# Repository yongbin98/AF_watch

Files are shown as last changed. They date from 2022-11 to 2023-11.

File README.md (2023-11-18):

# BAMI_watch

This repository contains the C code used in the PPG/ECG Wearable Devices for Atrial Fibrillation Diagnosis System thesis study. 

The code is designed for a smartwatch equipped with the following components:
- PPG sensor: MAX86171
- ECG sensor: MAX30003
- IMU sensor: LSM6DS
- LCD display: ST7789
- Battery monitoring chip: MAX17262
- Bluetooth module: E104-BT5005A
- Other components: SD card, switch, speaker

The following protocols are used:
- SD card: Fatfs
- ARM::CMSIS: ver 5.8.0
- ARM::DSP: ver 1.9.0

The hardware architectures:


The Developed wearable watch :


The code was developed in the Keil IDE.

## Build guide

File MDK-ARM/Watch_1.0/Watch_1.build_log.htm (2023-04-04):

µVision Build Log

Tool Versions:

IDE-Version: ¥ìVision V5.36.0.0
Copyright (C) 2021 ARM Ltd and ARM Germany GmbH. All rights reserved.
License Information: l l, l, LIC=3UURY-IHUXV-YDFK5-G8043-GK9D9-KWBGT
 
Tool Versions:
Toolchain:       MDK-ARM Professional  Version: 5.36.0.0
Toolchain Path:  C:\Keil_v5\ARM\ARMCC\Bin
C Compiler:      Armcc.exe V5.06 update 7 (build 960)
Assembler:       Armasm.exe V5.06 update 7 (build 960)
Linker/Locator:  ArmLink.exe V5.06 update 7 (build 960)
Library Manager: ArmAr.exe V5.06 update 7 (build 960)
Hex Converter:   FromElf.exe V5.06 update 7 (build 960)
CPU DLL:         SARMCM3.DLL V5.36.0.0
Dialog DLL:      DCM.DLL V1.17.3.0
Target DLL:      STLink\ST-LINKIII-KEIL_SWO.dll V3.0.9.0
Dialog DLL:      TCM.DLL V1.53.0.0

Project:

C:\Users\AW_Lab_LYB\Documents\STM32\Watch_V2.3 (Prototype)\MDK-ARM\Watch_1.0.uvprojx
Project File Date:  01/26/2023

Output:

*** Using Compiler 'V5.06 update 7 (build 960)', folder: 'C:\Keil_v5\ARM\ARMCC\Bin'
Build target 'Watch_1.0'
compiling MAX30003.c...
../Drivers/CMSIS/Device/ST/STM32F4xx/Include/stm32f413xx.h(52): warning:  #47-D: incompatible redefinition of macro "__FPU_PRESENT" 
  #define __FPU_PRESENT             1U       /*!< FPU present                                   */
..\Lib\MAX30003.c: 1 warning, 0 errors
compiling lcdscreen.c...
../Drivers/CMSIS/Device/ST/STM32F4xx/Include/stm32f413xx.h(52): warning:  #47-D: incompatible redefinition of macro "__FPU_PRESENT" 
  #define __FPU_PRESENT             1U       /*!< FPU present                                   */
..\Lib\lcdscreen.h(28): warning:  #1-D: last line of file ends without a newline
  #endif
..\Lib\lcdscreen.c(432): warning:  #1-D: last line of file ends without a newline
  }
..\Lib\lcdscreen.c: 3 warnings, 0 errors
linking...
Program Size: Code=86910 RO-data=247570 RW-data=252 ZI-data=181308  
FromELF: creating hex file...
"Watch_1.0\Watch_1.0" - 0 Error(s), 4 Warning(s).

Software Packages used:

Package Vendor: ARM
                http://www.keil.com/pack/ARM.CMSIS.5.8.0.pack
                ARM.CMSIS.5.8.0
                CMSIS (Common Microcontroller Software Interface Standard)
   * Component: CORE Version: 5.5.0

Package Vendor: Keil
                https://www.keil.com/pack/Keil.ARM_Compiler.1.7.1.pack
                Keil.ARM_Compiler.1.7.1
                Keil ARM Compiler extensions for ARM Compiler 5 and ARM Compiler 6
   * Component: STDERR Variant: ITM Version: 1.2.0
   * Component: STDIN Variant: ITM Version: 1.2.0
   * Component: STDOUT Variant: ITM Version: 1.2.0

Package Vendor: Keil
                http://www.keil.com/pack/Keil.STM32F4xx_DFP.2.16.0.pack
                Keil.STM32F4xx_DFP.2.16.0
                STMicroelectronics STM32F4 Series Device Support, Drivers and Examples

Collection of Component include folders:

  .\RTE\_Watch_1.0
  C:\Users\AW_Lab_LYB\AppData\Local\Arm\Packs\ARM\CMSIS\5.8.0\CMSIS\Core\Include
  C:\Users\AW_Lab_LYB\AppData\Local\Arm\Packs\Keil\STM32F4xx_DFP\2.16.0\Drivers\CMSIS\Device\ST\STM32F4xx\Include

Collection of Component Files used:

   * Component: ARM::CMSIS:CORE:5.5.0
      Include file:  CMSIS\Core\Include\tz_context.h

   * Component: Keil.ARM Compiler::Compiler:I/O:STDERR:ITM:1.2.0
      Source file:   Source\retarget_io.c

   * Component: Keil.ARM Compiler::Compiler:I/O:STDIN:ITM:1.2.0
      Source file:   Source\retarget_io.c

   * Component: Keil.ARM Compiler::Compiler:I/O:STDOUT:ITM:1.2.0
      Source file:   Source\retarget_io.c
Build Time Elapsed:  00:00:02

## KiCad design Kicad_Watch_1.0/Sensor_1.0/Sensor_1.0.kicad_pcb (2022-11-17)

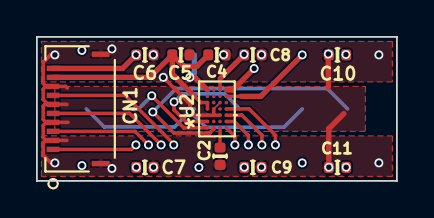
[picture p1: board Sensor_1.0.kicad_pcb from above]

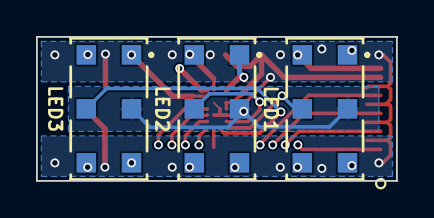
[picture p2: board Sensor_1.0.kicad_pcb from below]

Board: 4 copper layers, 20.0 x 8.0 mm, 14 parts (3 on the bottom side), 14 nets.

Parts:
C2: 1u; UL_C_0402_1005Metric
C4: 10u; UL_C_0402_1005Metric
C5: 0.1u; UL_C_0402_1005Metric
C6, C7, C8, C9, C10, C11: 22u; UL_C_0402_1005Metric
CN1: 503480-1000
LED1, LED2, LED3: SFH_7070; SFH7070
U2: MAX86171ENI+; MAX86171ENI&plus_

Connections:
+1V8: C4.1, C5.1, CN1.9, U2.D3 (VDD_ANA), U2.D4 (VDD_DIG)
/LED3_DRV: LED1.1, LED1.3, U2.A1 (LED3_DRV)
/LED4_DRV: LED2.1, LED2.3, U2.D1 (LED4_DRV)
/LED9_DRV: LED3.1, LED3.3, U2.A2 (LED9_DRV)
/PD1_IN: LED1.5, U2.D7 (PD1_IN)
/PD2_IN: LED2.5, U2.D6 (PD2_IN)
/PD3_IN: LED3.5, U2.C7 (PD3_IN)
/PPG_CS: CN1.7, U2.A7 (CSB/ADDR)
/PPG_MISO: CN1.3, U2.A5 (SDO)
/PPG_MOSI: CN1.5, U2.A6 (SDI/SDA)
/PPG_SCLK: CN1.1, U2.A4 (SCLK/SCL)
unnamed: C2.1, U2.B7 (VREF)
U_GND: C2.2, C4.2, C5.2, C6.2, C7.2, C8.2, C9.2, C10.2, C11.2, CN1.2, CN1.4, CN1.6, CN1.8, CN1.11, CN1.12, LED1.2, LED2.2, LED3.2, U2.B3 (PGND), U2.B5 (TRIG), U2.C4 (I2C_SEL), U2.C5 (GND), U2.D5 (PD_GND)
VDD: C6.1, C7.1, C8.1, C9.1, C10.1, C11.1, CN1.10, LED1.4, LED1.6, LED2.4, LED2.6, LED3.4, LED3.6, U2.B1 (VLED)

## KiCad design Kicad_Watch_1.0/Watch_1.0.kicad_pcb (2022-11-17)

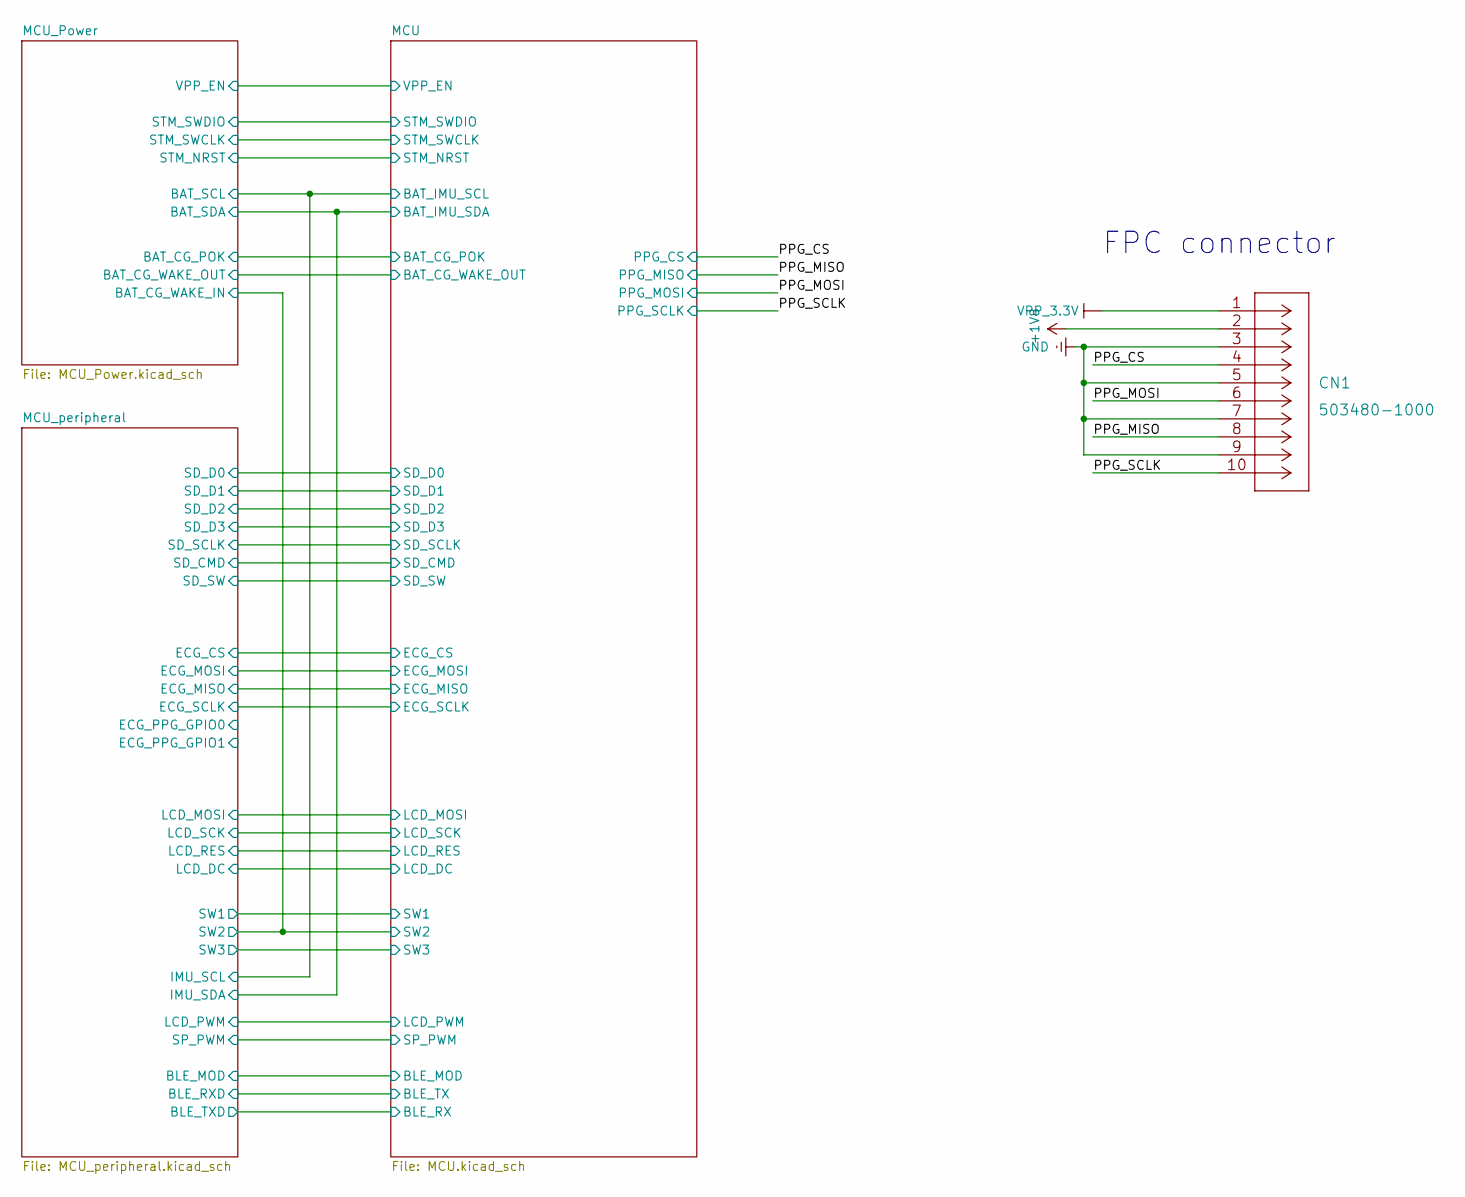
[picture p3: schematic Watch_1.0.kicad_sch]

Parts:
CN1: 503480-1000

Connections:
+1V8: CN1.2; also elsewhere on the board
/PPG_CS: CN1.4; also elsewhere on the board
/PPG_MISO: CN1.8; also elsewhere on the board
/PPG_MOSI: CN1.6; also elsewhere on the board
/PPG_SCLK: CN1.10; also elsewhere on the board
U_GND: CN1.3, CN1.5, CN1.7, CN1.9, CN1.11, CN1.12; also elsewhere on the board
VPP_3_3V: CN1.1; also elsewhere on the board

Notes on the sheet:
FPC connector

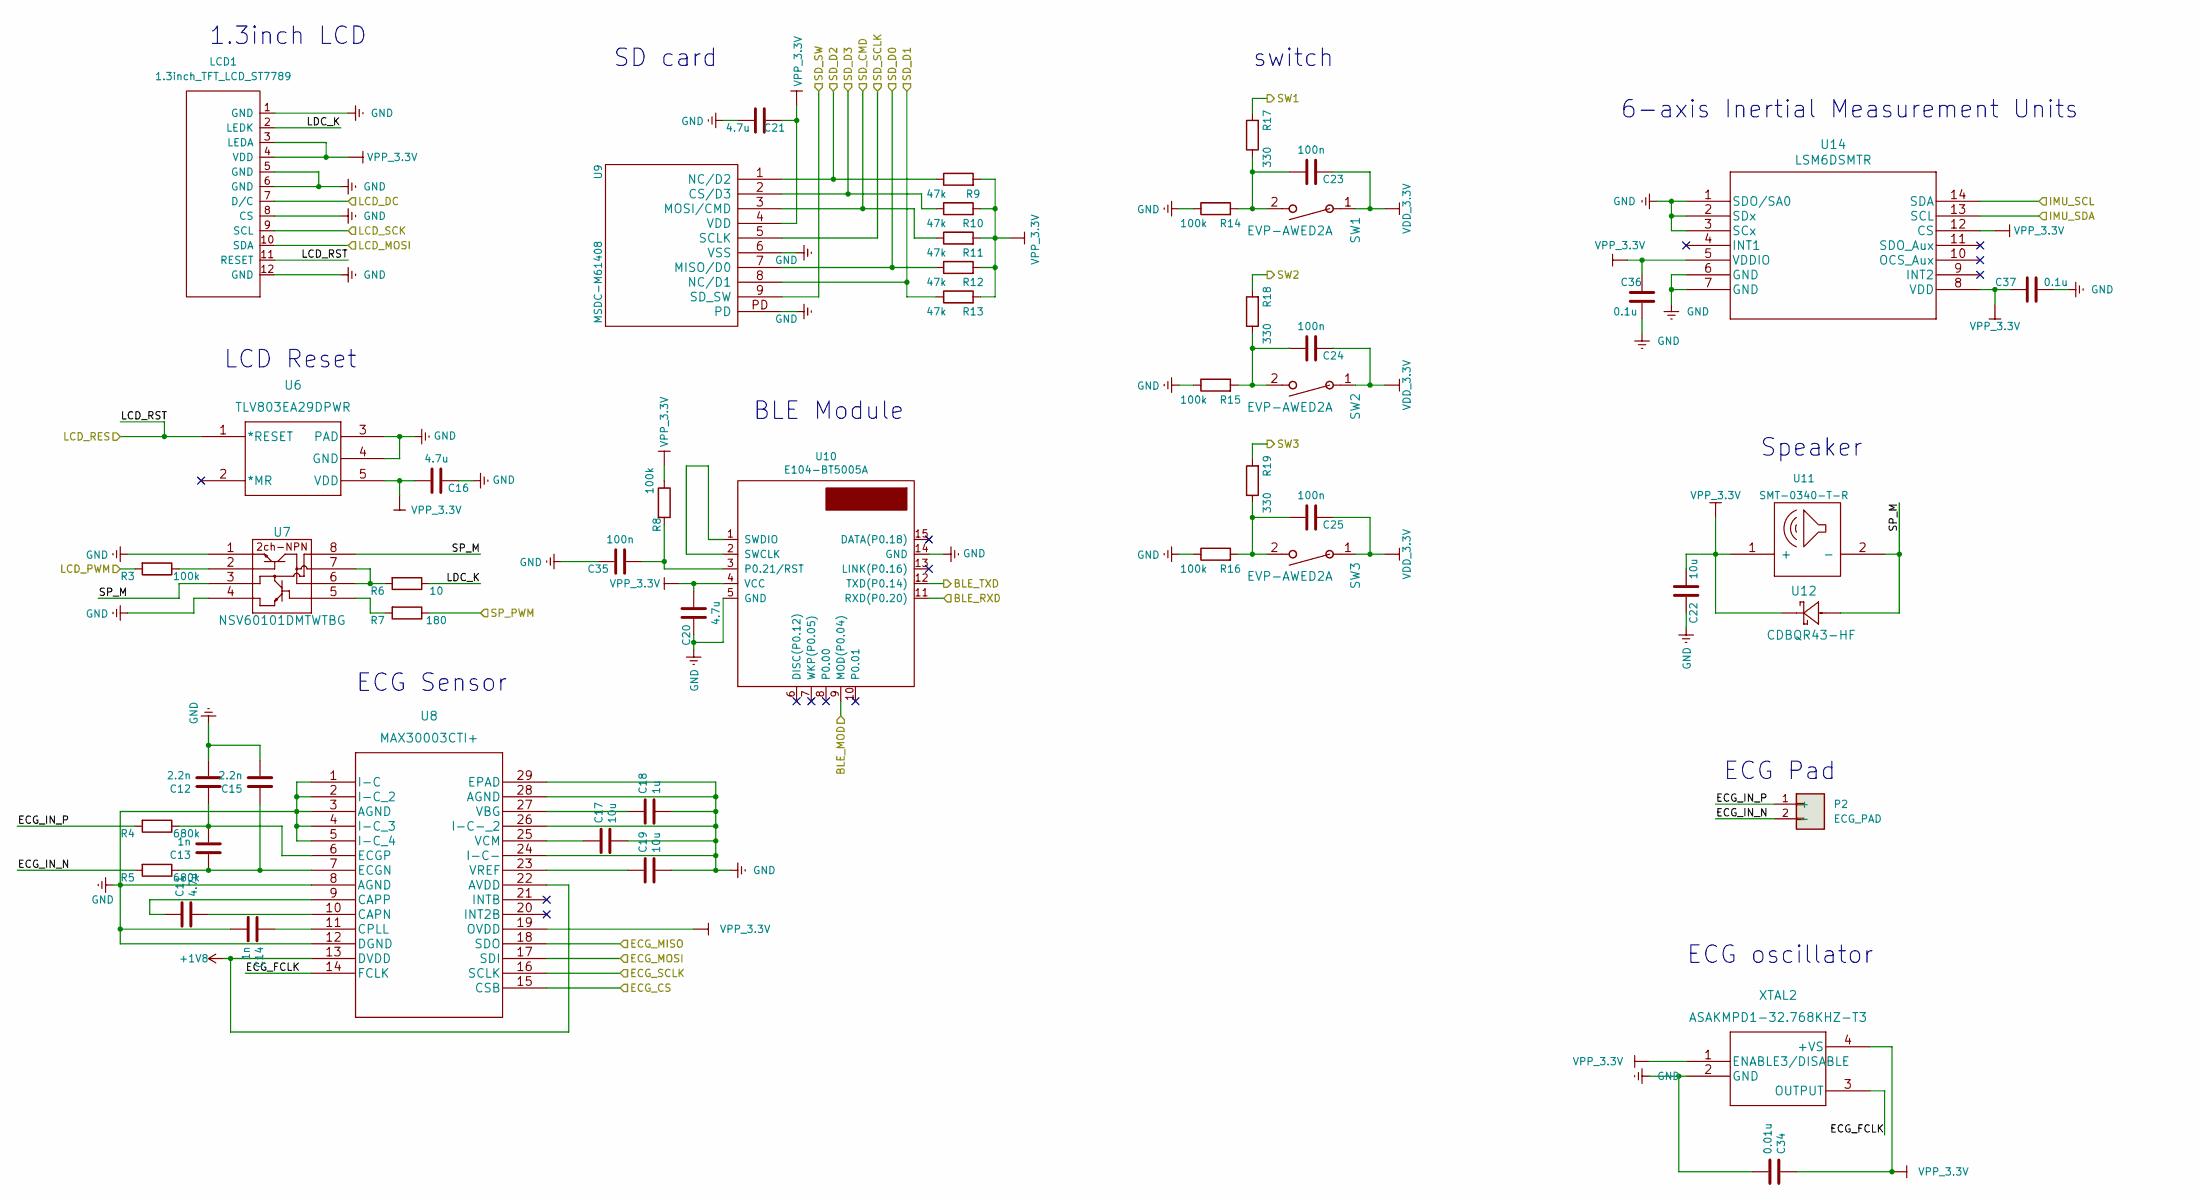
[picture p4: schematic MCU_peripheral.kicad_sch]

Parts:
C11, C16, C20, C21: 4.7u; UL_C_0402_1005Metric
C12, C15: 2.2n; UL_C_0402_1005Metric
C13, C14: 1n; UL_C_0402_1005Metric
C17, C19, C22: 10u; UL_C_0402_1005Metric
C18: 1u; UL_C_0402_1005Metric
C23, C24, C25, C35: 100n; UL_C_0402_1005Metric
C34: 0.01u; UL_C_0402_1005Metric
C36, C37: 0.1u; UL_C_0402_1005Metric
LCD1: 1.3inch_TFT_LCD_ST7789
P2: ECG_PAD
R3, R8, R14, R15, R16: 100k; R_0402_1005Metric
R4, R5: 680k; R_0402_1005Metric
R6: 10; R_0402_1005Metric
R7: 180; R_0402_1005Metric
R9, R10, R11, R12, R13: 47k; R_0402_1005Metric
R17, R18, R19: 330; R_0402_1005Metric
SW1, SW2, SW3: EVP-AWED2A
U6: TLV803EA29DPWR
U7: NSV60101DMTWTBG
U8: MAX30003CTI+; MAX30003CTI&plus_
U9: MSDC-M61408; MSDC-M61408(Micro_SD)
U10: E104-BT5005A; E104-BT5005A_QFN-15_9x9_Pitch1.1mm
U11: SMT-0340-T-R
U12: CDBQR43-HF
U14: LSM6DSMTR
XTAL2: ASAKMPD1-32.768KHZ-T3

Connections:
+1V8: U8.13 (DVDD), U8.22 (AVDD); also elsewhere on the board
/MCU/BAT_IMU_SCL: U14.14 (SDA); also elsewhere on the board
/MCU/BAT_IMU_SDA: U14.13 (SCL); also elsewhere on the board
/MCU/BLE_MOD: U10.9 (MOD(P0.04)); also elsewhere on the board
/MCU/BLE_RX: U10.12 (TXD(P0.14)); also elsewhere on the board
/MCU/BLE_TX: U10.11 (RXD(P0.20)); also elsewhere on the board
/MCU/ECG_CS: U8.15 (CSB); also elsewhere on the board
/MCU/ECG_MISO: U8.18 (SDO); also elsewhere on the board
/MCU/ECG_MOSI: U8.17 (SDI); also elsewhere on the board
/MCU/ECG_SCLK: U8.16 (SCLK); also elsewhere on the board
/MCU/LCD_DC: LCD1.7 (D/C); also elsewhere on the board
/MCU/LCD_MOSI: LCD1.10 (SDA); also elsewhere on the board
/MCU/LCD_PWM: R3.2; also elsewhere on the board
/MCU/LCD_SCK: LCD1.9 (SCL); also elsewhere on the board
/MCU/SD_CMD: R11.1, U9.3 (MOSI/CMD); also elsewhere on the board
/MCU/SD_D0: R12.1, U9.7 (MISO/D0); also elsewhere on the board
/MCU/SD_D1: R13.1, U9.8 (NC/D1); also elsewhere on the board
/MCU/SD_D2: R9.1, U9.1 (NC/D2); also elsewhere on the board
/MCU/SD_D3: R10.1, U9.2 (CS/D3); also elsewhere on the board
/MCU/SD_SCLK: U9.5 (SCLK); also elsewhere on the board
/MCU/SD_SW: U9.9 (SD_SW); also elsewhere on the board
/MCU/SP_PWM: R7.1; also elsewhere on the board
/MCU/SW1: R17.2; also elsewhere on the board
/MCU/SW2: R18.2; also elsewhere on the board
/MCU/SW3: R19.2; also elsewhere on the board
/MCU_peripheral/ECG_FCLK: U8.14 (FCLK), XTAL2.3 (OUTPUT)
/MCU_peripheral/ECG_IN_N: P2.2 (-), R5.2
/MCU_peripheral/ECG_IN_P: P2.1 (+), R4.2
/MCU_peripheral/LCD_RST: LCD1.11 (RESET), U6.1 (*RESET); also elsewhere on the board
/MCU_peripheral/LDC_K: LCD1.2 (LEDK), R6.1
/MCU_peripheral/SP_M: U7.3, U7.8, U11.2 (-), U12.2
unnamed: C11.1, U8.9 (CAPP)
unnamed: C11.2, U8.10 (CAPN)
unnamed: C12.1, C13.2, R4.1, U8.6 (ECGP)
unnamed: C13.1, C15.1, R5.1, U8.7 (ECGN)
unnamed: C14.1, U8.11 (CPLL)
unnamed: C17.1, U8.25 (VCM)
unnamed: C18.1, U8.27 (VBG)
unnamed: C19.1, U8.23 (VREF)
unnamed: C23.2, R14.2, R17.1, SW1.2
unnamed: C24.2, R15.2, R18.1, SW2.2
unnamed: C25.2, R16.2, R19.1, SW3.2
unnamed: C35.2, R8.2, U10.3 (P0.21/RST)
unnamed: R3.1, U7.2
unnamed: R6.2, U7.6, U7.7
unnamed: R7.2, U7.5
unnamed: U10.1 (SWDIO), U10.2 (SWCLK)
U_GND: C12.2, C14.2, C15.2, C16.1, C17.2, C18.2, C19.2, C20.1, C21.1, C22.1, C34.2, C35.1, C36.2, C37.2, LCD1.1 (GND), LCD1.5 (GND), LCD1.6 (GND), LCD1.8 (CS), LCD1.12 (GND), R14.1, R15.1, R16.1, U6.3 (PAD), U6.4 (GND), U7.1, U7.4, U8.1 (I-C), U8.2 (I-C_2), U8.3 (AGND), U8.4 (I-C_3), U8.5 (I-C_4), U8.8 (AGND), U8.12 (DGND), U8.24 (I-C-), U8.26 (I-C-_2), U8.28 (AGND), U8.29 (EPAD), U9.6 (VSS), U9.PD, U10.5 (GND), U10.14 (GND), U14.1 (SDO/SA0), U14.2 (SDx), U14.3 (SCx), U14.6 (GND), U14.7 (GND), XTAL2.2 (GND); also elsewhere on the board
VDD_3_3V: C23.1, C24.1, C25.1, SW1.1, SW2.1, SW3.1; also elsewhere on the board
VPP_3_3V: C16.2, C20.2, C21.2, C22.2, C34.1, C36.1, C37.1, LCD1.3 (LEDA), LCD1.4 (VDD), R8.1, R9.2, R10.2, R11.2, R12.2, R13.2, U6.5 (VDD), U8.19 (OVDD), U9.4 (VDD), U10.4 (VCC), U11.1 (+), U12.1, U14.5 (VDDIO), U14.8 (VDD), U14.12 (CS), XTAL2.1 (ENABLE3/DISABLE), XTAL2.4 (+VS); also elsewhere on the board

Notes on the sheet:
6-axis Inertial Measurement Units
Speaker
switch
ECG Pad
1.3inch LCD
LCD Reset
BLE Module
SD card
ECG oscillator
ECG Sensor

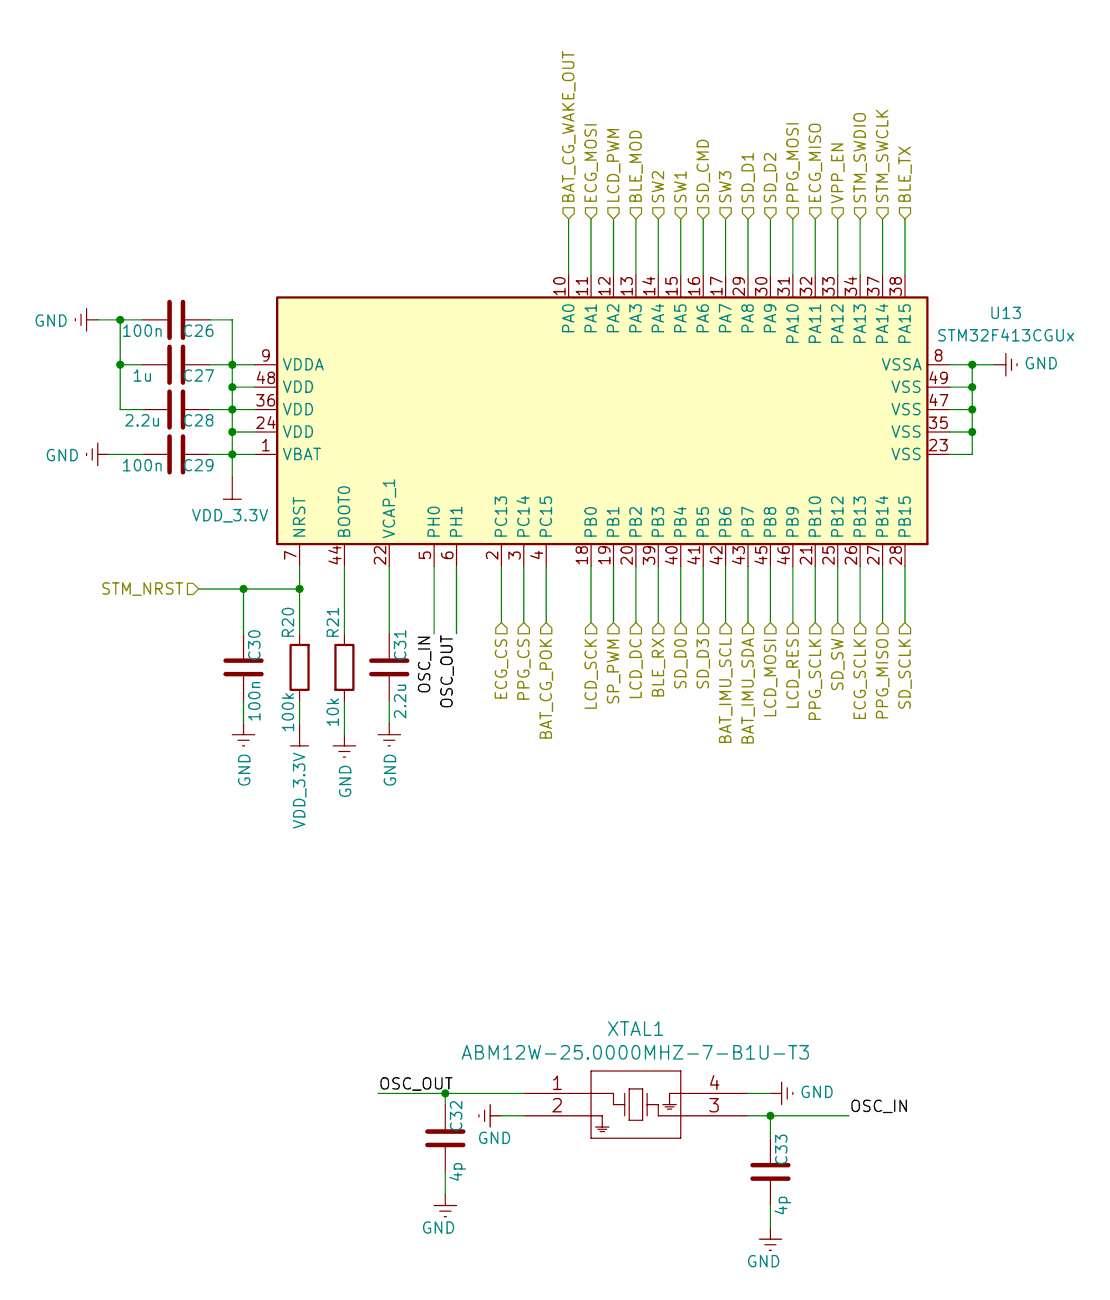
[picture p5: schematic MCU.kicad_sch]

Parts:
C26, C29, C30: 100n; UL_C_0402_1005Metric
C27: 1u; UL_C_0402_1005Metric
C28, C31: 2.2u; UL_C_0402_1005Metric
C32, C33: 4p; UL_C_0402_1005Metric
R20: 100k; R_0402_1005Metric
R21: 10k; R_0402_1005Metric
U13: STM32F413CGUx; QFN-48-1EP_7x7mm_P0.5mm_EP5.6x5.6mm
XTAL1: ABM12W-25.0000MHZ-7-B1U-T3; ABM12W

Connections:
/MCU/BAT_CG_POK: U13.4 (PC15); also elsewhere on the board
/MCU/BAT_CG_WAKE_OUT: U13.10 (PA0); also elsewhere on the board
/MCU/BAT_IMU_SCL: U13.42 (PB6); also elsewhere on the board
/MCU/BAT_IMU_SDA: U13.43 (PB7); also elsewhere on the board
/MCU/BLE_MOD: U13.13 (PA3); also elsewhere on the board
/MCU/BLE_RX: U13.39 (PB3); also elsewhere on the board
/MCU/BLE_TX: U13.38 (PA15); also elsewhere on the board
/MCU/ECG_CS: U13.2 (PC13); also elsewhere on the board
/MCU/ECG_MISO: U13.32 (PA11); also elsewhere on the board
/MCU/ECG_MOSI: U13.11 (PA1); also elsewhere on the board
/MCU/ECG_SCLK: U13.26 (PB13); also elsewhere on the board
/MCU/LCD_DC: U13.20 (PB2); also elsewhere on the board
/MCU/LCD_MOSI: U13.45 (PB8); also elsewhere on the board
/MCU/LCD_PWM: U13.12 (PA2); also elsewhere on the board
/MCU/LCD_SCK: U13.18 (PB0); also elsewhere on the board
/MCU/OSC_IN: C33.2, U13.5 (PH0), XTAL1.3
/MCU/OSC_OUT: C32.2, U13.6 (PH1), XTAL1.1
/MCU/SD_CMD: U13.16 (PA6); also elsewhere on the board
/MCU/SD_D0: U13.40 (PB4); also elsewhere on the board
/MCU/SD_D1: U13.29 (PA8); also elsewhere on the board
/MCU/SD_D2: U13.30 (PA9); also elsewhere on the board
/MCU/SD_D3: U13.41 (PB5); also elsewhere on the board
/MCU/SD_SCLK: U13.28 (PB15); also elsewhere on the board
/MCU/SD_SW: U13.25 (PB12); also elsewhere on the board
/MCU/SP_PWM: U13.19 (PB1); also elsewhere on the board
/MCU/STM_NRST: C30.2, R20.2, U13.7 (NRST); also elsewhere on the board
/MCU/STM_SWCLK: U13.37 (PA14); also elsewhere on the board
/MCU/STM_SWDIO: U13.34 (PA13); also elsewhere on the board
/MCU/SW1: U13.15 (PA5); also elsewhere on the board
/MCU/SW2: U13.14 (PA4); also elsewhere on the board
/MCU/SW3: U13.17 (PA7); also elsewhere on the board
/MCU/VPP_EN: U13.33 (PA12); also elsewhere on the board
/MCU_peripheral/LCD_RST: U13.46 (PB9); also elsewhere on the board
/PPG_CS: U13.3 (PC14); also elsewhere on the board
/PPG_MISO: U13.27 (PB14); also elsewhere on the board
/PPG_MOSI: U13.31 (PA10); also elsewhere on the board
/PPG_SCLK: U13.21 (PB10); also elsewhere on the board
unnamed: C31.2, U13.22 (VCAP_1)
unnamed: R21.1, U13.44 (BOOT0)
U_GND: C26.1, C27.1, C28.1, C29.1, C30.1, C31.1, C32.1, C33.1, R21.2, U13.8 (VSSA), U13.23 (VSS), U13.35 (VSS), U13.47 (VSS), U13.49 (VSS), XTAL1.2, XTAL1.4; also elsewhere on the board
VDD_3_3V: C26.2, C27.2, C28.2, C29.2, R20.1, U13.1 (VBAT), U13.9 (VDDA), U13.24 (VDD), U13.36 (VDD), U13.48 (VDD); also elsewhere on the board

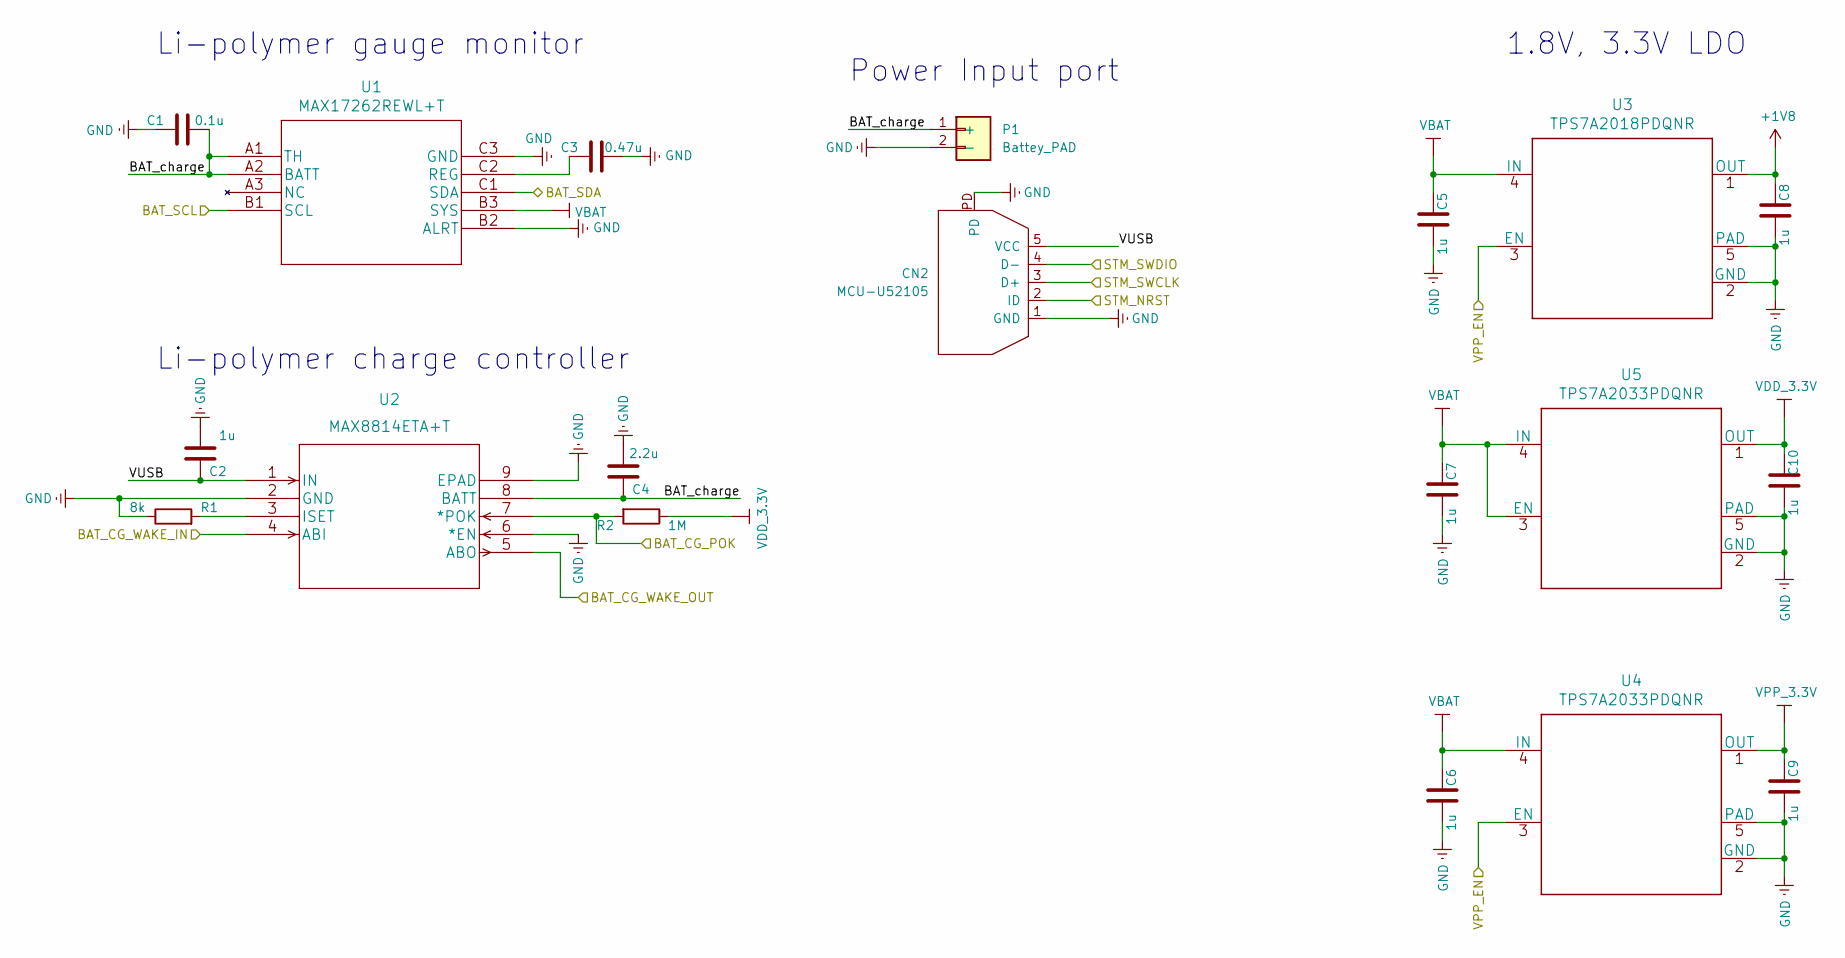
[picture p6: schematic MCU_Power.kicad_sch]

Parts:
C1: 0.1u; UL_C_0402_1005Metric
C2, C5, C6, C7, C8, C9, C10: 1u; UL_C_0402_1005Metric
C3: 0.47u; UL_C_0402_1005Metric
C4: 2.2u; UL_C_0402_1005Metric
CN2: MCU-U52105
P1: Battey_PAD
R1: 8k; R_0402_1005Metric
R2: 1M; R_0402_1005Metric
U1: MAX17262REWL+T; MAX17262REWL&plus_T
U2: MAX8814ETA+T; MAX8814ETA&plus_T
U3: TPS7A2018PDQNR; X2SON-4PIN
U4, U5: TPS7A2033PDQNR; X2SON-4PIN

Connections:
+1V8: C8.2, U3.1 (OUT); also elsewhere on the board
/MCU/BAT_CG_POK: R2.2, U2.7 (*POK); also elsewhere on the board
/MCU/BAT_CG_WAKE_OUT: U2.5 (ABO); also elsewhere on the board
/MCU/BAT_IMU_SCL: U1.B1 (SCL); also elsewhere on the board
/MCU/BAT_IMU_SDA: U1.C1 (SDA); also elsewhere on the board
/MCU/STM_NRST: CN2.2 (ID); also elsewhere on the board
/MCU/STM_SWCLK: CN2.3 (D+); also elsewhere on the board
/MCU/STM_SWDIO: CN2.4 (D-); also elsewhere on the board
/MCU/SW2: U2.4 (ABI); also elsewhere on the board
/MCU/VPP_EN: U3.3 (EN), U4.3 (EN); also elsewhere on the board
/MCU_Power/BAT_charge: C1.2, C4.1, P1.1 (+), U1.A1 (TH), U1.A2 (BATT), U2.8 (BATT)
/MCU_Power/VUSB: C2.1, CN2.5 (VCC), U2.1 (IN)
unnamed: C3.2, U1.C2 (REG)
unnamed: R1.2, U2.3 (ISET)
U_GND: C1.1, C2.2, C3.1, C4.2, C5.1, C6.1, C7.1, C8.1, C9.1, C10.1, CN2.1 (GND), CN2.PD, P1.2 (-), R1.1, U1.B2 (ALRT), U1.C3 (GND), U2.2 (GND), U2.6 (*EN), U2.9 (EPAD), U3.2 (GND), U3.5 (PAD), U4.2 (GND), U4.5 (PAD), U5.2 (GND), U5.5 (PAD); also elsewhere on the board
VBAT: C5.2, C6.2, C7.2, U1.B3 (SYS), U3.4 (IN), U4.4 (IN), U5.3 (EN), U5.4 (IN)
VDD_3_3V: C10.2, R2.1, U5.1 (OUT); also elsewhere on the board
VPP_3_3V: C9.2, U4.1 (OUT); also elsewhere on the board

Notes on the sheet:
Li-polymer charge controller
Li-polymer gauge monitor
1.8V, 3.3V LDO
Power Input port

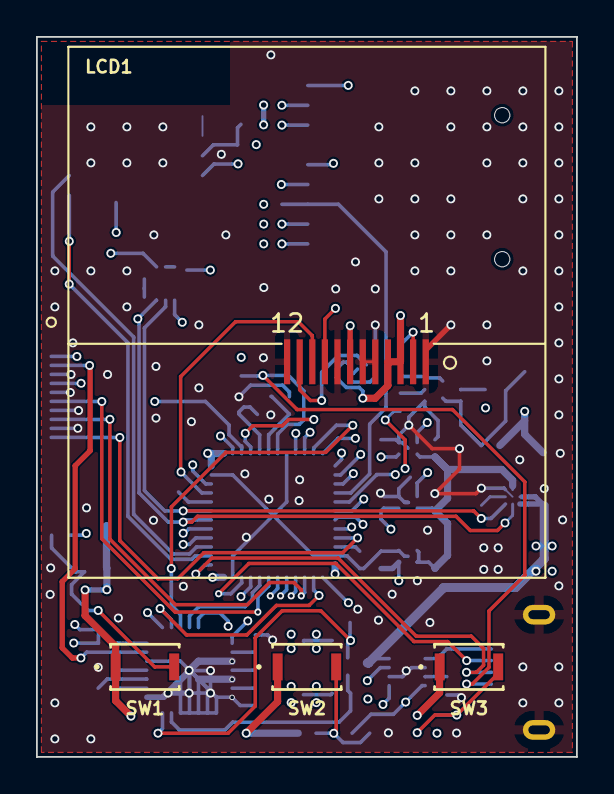
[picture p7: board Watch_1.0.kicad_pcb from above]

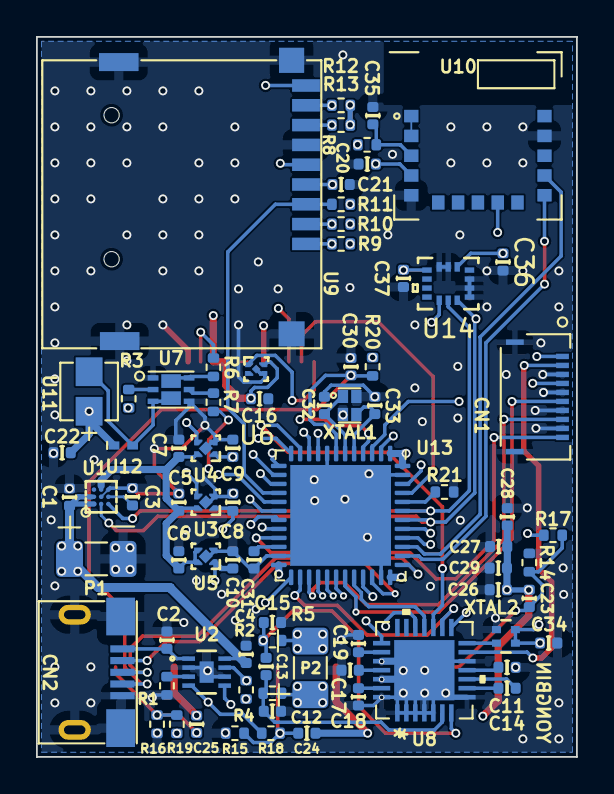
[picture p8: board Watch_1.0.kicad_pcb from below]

Board: 4 copper layers, 30.0 x 40.0 mm, 82 parts (78 on the bottom side), 69 nets.

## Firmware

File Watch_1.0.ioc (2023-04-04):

#MicroXplorer Configuration settings - do not modify
Dma.Request0=SDIO_RX
Dma.Request1=SDIO_TX
Dma.Request2=SPI2_RX
Dma.Request3=SPI2_TX
Dma.Request4=SPI4_RX
Dma.Request5=SPI4_TX
Dma.Request6=UART7_TX
Dma.Request7=SPI5_TX
Dma.Request8=SPI5_RX
Dma.RequestsNb=9
Dma.SDIO_RX.0.Direction=DMA_PERIPH_TO_MEMORY
Dma.SDIO_RX.0.FIFOMode=DMA_FIFOMODE_ENABLE
Dma.SDIO_RX.0.FIFOThreshold=DMA_FIFO_THRESHOLD_FULL
Dma.SDIO_RX.0.Instance=DMA2_Stream3
Dma.SDIO_RX.0.MemBurst=DMA_MBURST_INC4
Dma.SDIO_RX.0.MemDataAlignment=DMA_MDATAALIGN_WORD
Dma.SDIO_RX.0.MemInc=DMA_MINC_ENABLE
Dma.SDIO_RX.0.Mode=DMA_PFCTRL
Dma.SDIO_RX.0.PeriphBurst=DMA_PBURST_INC4
Dma.SDIO_RX.0.PeriphDataAlignment=DMA_PDATAALIGN_WORD
Dma.SDIO_RX.0.PeriphInc=DMA_PINC_DISABLE
Dma.SDIO_RX.0.Priority=DMA_PRIORITY_LOW
Dma.SDIO_RX.0.RequestParameters=Instance,Direction,PeriphInc,MemInc,PeriphDataAlignment,MemDataAlignment,Mode,Priority,FIFOMode,FIFOThreshold,MemBurst,PeriphBurst
Dma.SDIO_TX.1.Direction=DMA_MEMORY_TO_PERIPH
Dma.SDIO_TX.1.FIFOMode=DMA_FIFOMODE_ENABLE
Dma.SDIO_TX.1.FIFOThreshold=DMA_FIFO_THRESHOLD_FULL
Dma.SDIO_TX.1.Instance=DMA2_Stream6
Dma.SDIO_TX.1.MemBurst=DMA_MBURST_INC4
Dma.SDIO_TX.1.MemDataAlignment=DMA_MDATAALIGN_WORD
Dma.SDIO_TX.1.MemInc=DMA_MINC_ENABLE
Dma.SDIO_TX.1.Mode=DMA_PFCTRL
Dma.SDIO_TX.1.PeriphBurst=DMA_PBURST_INC4
Dma.SDIO_TX.1.PeriphDataAlignment=DMA_PDATAALIGN_WORD
Dma.SDIO_TX.1.PeriphInc=DMA_PINC_DISABLE
Dma.SDIO_TX.1.Priority=DMA_PRIORITY_LOW
Dma.SDIO_TX.1.RequestParameters=Instance,Direction,PeriphInc,MemInc,PeriphDataAlignment,MemDataAlignment,Mode,Priority,FIFOMode,FIFOThreshold,MemBurst,PeriphBurst
Dma.SPI2_RX.2.Direction=DMA_PERIPH_TO_MEMORY
Dma.SPI2_RX.2.FIFOMode=DMA_FIFOMODE_DISABLE
Dma.SPI2_RX.2.Instance=DMA1_Stream3
Dma.SPI2_RX.2.MemDataAlignment=DMA_MDATAALIGN_BYTE
Dma.SPI2_RX.2.MemInc=DMA_MINC_ENABLE
Dma.SPI2_RX.2.Mode=DMA_NORMAL
Dma.SPI2_RX.2.PeriphDataAlignment=DMA_PDATAALIGN_BYTE
Dma.SPI2_RX.2.PeriphInc=DMA_PINC_DISABLE
Dma.SPI2_RX.2.Priority=DMA_PRIORITY_LOW
Dma.SPI2_RX.2.RequestParameters=Instance,Direction,PeriphInc,MemInc,PeriphDataAlignment,MemDataAlignment,Mode,Priority,FIFOMode
Dma.SPI2_TX.3.Direction=DMA_MEMORY_TO_PERIPH
Dma.SPI2_TX.3.FIFOMode=DMA_FIFOMODE_DISABLE
Dma.SPI2_TX.3.Instance=DMA1_Stream4
Dma.SPI2_TX.3.MemDataAlignment=DMA_MDATAALIGN_BYTE
Dma.SPI2_TX.3.MemInc=DMA_MINC_ENABLE
Dma.SPI2_TX.3.Mode=DMA_NORMAL
Dma.SPI2_TX.3.PeriphDataAlignment=DMA_PDATAALIGN_BYTE
Dma.SPI2_TX.3.PeriphInc=DMA_PINC_DISABLE
Dma.SPI2_TX.3.Priority=DMA_PRIORITY_LOW
Dma.SPI2_TX.3.RequestParameters=Instance,Direction,PeriphInc,MemInc,PeriphDataAlignment,MemDataAlignment,Mode,Priority,FIFOMode
Dma.SPI4_RX.4.Direction=DMA_PERIPH_TO_MEMORY
Dma.SPI4_RX.4.FIFOMode=DMA_FIFOMODE_DISABLE
Dma.SPI4_RX.4.Instance=DMA2_Stream0
Dma.SPI4_RX.4.MemDataAlignment=DMA_MDATAALIGN_BYTE
Dma.SPI4_RX.4.MemInc=DMA_MINC_ENABLE
Dma.SPI4_RX.4.Mode=DMA_NORMAL
Dma.SPI4_RX.4.PeriphDataAlignment=DMA_PDATAALIGN_BYTE
Dma.SPI4_RX.4.PeriphInc=DMA_PINC_DISABLE
Dma.SPI4_RX.4.Priority=DMA_PRIORITY_LOW
Dma.SPI4_RX.4.RequestParameters=Instance,Direction,PeriphInc,MemInc,PeriphDataAlignment,MemDataAlignment,Mode,Priority,FIFOMode
Dma.SPI4_TX.5.Direction=DMA_MEMORY_TO_PERIPH
Dma.SPI4_TX.5.FIFOMode=DMA_FIFOMODE_DISABLE
Dma.SPI4_TX.5.Instance=DMA2_Stream1
Dma.SPI4_TX.5.MemDataAlignment=DMA_MDATAALIGN_BYTE
Dma.SPI4_TX.5.MemInc=DMA_MINC_ENABLE
Dma.SPI4_TX.5.Mode=DMA_NORMAL
Dma.SPI4_TX.5.PeriphDataAlignment=DMA_PDATAALIGN_BYTE
Dma.SPI4_TX.5.PeriphInc=DMA_PINC_DISABLE
Dma.SPI4_TX.5.Priority=DMA_PRIORITY_LOW
Dma.SPI4_TX.5.RequestParameters=Instance,Direction,PeriphInc,MemInc,PeriphDataAlignment,MemDataAlignment,Mode,Priority,FIFOMode
Dma.SPI5_RX.8.Direction=DMA_PERIPH_TO_MEMORY
Dma.SPI5_RX.8.FIFOMode=DMA_FIFOMODE_DISABLE
Dma.SPI5_RX.8.Instance=DMA2_Stream5
Dma.SPI5_RX.8.MemDataAlignment=DMA_MDATAALIGN_BYTE
Dma.SPI5_RX.8.MemInc=DMA_MINC_ENABLE
Dma.SPI5_RX.8.Mode=DMA_NORMAL
Dma.SPI5_RX.8.PeriphDataAlignment=DMA_PDATAALIGN_BYTE
Dma.SPI5_RX.8.PeriphInc=DMA_PINC_DISABLE
Dma.SPI5_RX.8.Priority=DMA_PRIORITY_LOW
Dma.SPI5_RX.8.RequestParameters=Instance,Direction,PeriphInc,MemInc,PeriphDataAlignment,MemDataAlignment,Mode,Priority,FIFOMode
Dma.SPI5_TX.7.Direction=DMA_MEMORY_TO_PERIPH
Dma.SPI5_TX.7.FIFOMode=DMA_FIFOMODE_DISABLE
Dma.SPI5_TX.7.Instance=DMA2_Stream4
Dma.SPI5_TX.7.MemDataAlignment=DMA_MDATAALIGN_BYTE
Dma.SPI5_TX.7.MemInc=DMA_MINC_ENABLE
Dma.SPI5_TX.7.Mode=DMA_NORMAL
Dma.SPI5_TX.7.PeriphDataAlignment=DMA_PDATAALIGN_BYTE
Dma.SPI5_TX.7.PeriphInc=DMA_PINC_DISABLE
Dma.SPI5_TX.7.Priority=DMA_PRIORITY_LOW
Dma.SPI5_TX.7.RequestParameters=Instance,Direction,PeriphInc,MemInc,PeriphDataAlignment,MemDataAlignment,Mode,Priority,FIFOMode
Dma.UART7_TX.6.Direction=DMA_MEMORY_TO_PERIPH
Dma.UART7_TX.6.FIFOMode=DMA_FIFOMODE_DISABLE
Dma.UART7_TX.6.Instance=DMA1_Stream1
Dma.UART7_TX.6.MemDataAlignment=DMA_MDATAALIGN_BYTE
Dma.UART7_TX.6.MemInc=DMA_MINC_ENABLE
Dma.UART7_TX.6.Mode=DMA_NORMAL
Dma.UART7_TX.6.PeriphDataAlignment=DMA_PDATAALIGN_BYTE
Dma.UART7_TX.6.PeriphInc=DMA_PINC_DISABLE
Dma.UART7_TX.6.Priority=DMA_PRIORITY_LOW
Dma.UART7_TX.6.RequestParameters=Instance,Direction,PeriphInc,MemInc,PeriphDataAlignment,MemDataAlignment,Mode,Priority,FIFOMode
FATFS.BSP.number=1
FATFS.IPParameters=_MAX_SS,_FS_LOCK,USE_DMA_CODE_SD,_USE_LFN,_USE_FIND,_CODE_PAGE,_LFN_UNICODE,_STRF_ENCODE
FATFS.USE_DMA_CODE_SD=1
FATFS._CODE_PAGE=850
FATFS._FS_LOCK=5
FATFS._LFN_UNICODE=0
FATFS._MAX_SS=4096
FATFS._STRF_ENCODE=3
FATFS._USE_FIND=1
FATFS._USE_LFN=1
FATFS0.BSP.STBoard=false
FATFS0.BSP.api=Unknown
FATFS0.BSP.component=
FATFS0.BSP.condition=
FATFS0.BSP.i2caddr=0
FATFS0.BSP.i2creg=
FATFS0.BSP.instance=PB12
FATFS0.BSP.ip=GPIO
FATFS0.BSP.mode=Input
FATFS0.BSP.name=Detect_SDIO
FATFS0.BSP.semaphore=
FATFS0.BSP.solution=PB12
File.Version=6
GPIO.groupedBy=Group By Peripherals
I2C1.I2C_Mode=I2C_Fast
I2C1.IPParameters=I2C_Mode
IWDG.IPParameters=Prescaler
IWDG.Prescaler=IWDG_PRESCALER_64
KeepUserPlacement=false
Mcu.CPN=STM32F413CGU3
Mcu.Family=STM32F4
Mcu.IP0=DMA
Mcu.IP1=FATFS
Mcu.IP10=SYS
Mcu.IP11=TIM3
Mcu.IP12=TIM6
Mcu.IP13=TIM7
Mcu.IP14=TIM9
Mcu.IP15=UART7
Mcu.IP2=I2C1
Mcu.IP3=IWDG
Mcu.IP4=NVIC
Mcu.IP5=RCC
Mcu.IP6=SDIO
Mcu.IP7=SPI2
Mcu.IP8=SPI4
Mcu.IP9=SPI5
Mcu.IPNb=16
Mcu.Name=STM32F413C(G-H)Ux
Mcu.Package=UFQFPN48
Mcu.Pin0=PC13
Mcu.Pin1=PC14-OSC32_IN
Mcu.Pin10=PA5
Mcu.Pin11=PA6
Mcu.Pin12=PA7
Mcu.Pin13=PB0
Mcu.Pin14=PB1
Mcu.Pin15=PB2
Mcu.Pin16=PB10
Mcu.Pin17=PB12
Mcu.Pin18=PB13
Mcu.Pin19=PB14
Mcu.Pin2=PC15-OSC32_OUT
Mcu.Pin20=PB15
Mcu.Pin21=PA8
Mcu.Pin22=PA9
Mcu.Pin23=PA10
Mcu.Pin24=PA11
Mcu.Pin25=PA12
Mcu.Pin26=PA13
Mcu.Pin27=PA14
Mcu.Pin28=PA15
Mcu.Pin29=PB3
Mcu.Pin3=PH0 - OSC_IN
Mcu.Pin30=PB4
Mcu.Pin31=PB5
Mcu.Pin32=PB6
Mcu.Pin33=PB7
Mcu.Pin34=PB8
Mcu.Pin35=PB9
Mcu.Pin36=VP_FATFS_VS_SDIO
Mcu.Pin37=VP_IWDG_VS_IWDG
Mcu.Pin38=VP_SYS_VS_tim1
Mcu.Pin39=VP_TIM6_VS_ClockSourceINT
Mcu.Pin4=PH1 - OSC_OUT
Mcu.Pin40=VP_TIM7_VS_ClockSourceINT
Mcu.Pin5=PA0
Mcu.Pin6=PA1
Mcu.Pin7=PA2
Mcu.Pin8=PA3
Mcu.Pin9=PA4
Mcu.PinsNb=41
Mcu.ThirdPartyNb=0
Mcu.UserConstants=
Mcu.UserName=STM32F413CGUx
MxCube.Version=6.5.0
MxDb.Version=DB.6.0.50
NVIC.BusFault_IRQn=true\:0\:0\:false\:false\:true\:false\:false\:true
NVIC.DMA1_Stream1_IRQn=true\:0\:0\:false\:false\:true\:false\:true\:true
NVIC.DMA1_Stream3_IRQn=true\:0\:0\:false\:false\:true\:false\:true\:true
NVIC.DMA1_Stream4_IRQn=true\:0\:0\:true\:false\:true\:false\:true\:true
NVIC.DMA2_Stream0_IRQn=true\:0\:0\:false\:false\:true\:false\:true\:true
NVIC.DMA2_Stream1_IRQn=true\:0\:0\:false\:false\:true\:false\:true\:true
NVIC.DMA2_Stream3_IRQn=true\:0\:0\:false\:false\:true\:false\:true\:true
NVIC.DMA2_Stream4_IRQn=true\:0\:0\:false\:false\:true\:false\:true\:true
NVIC.DMA2_Stream5_IRQn=true\:0\:0\:false\:false\:true\:false\:true\:true
NVIC.DMA2_Stream6_IRQn=true\:0\:0\:false\:false\:true\:false\:true\:true
NVIC.DebugMonitor_IRQn=true\:0\:0\:false\:false\:true\:false\:false\:true
NVIC.EXTI4_IRQn=true\:0\:0\:false\:false\:true\:true\:true\:true
NVIC.EXTI9_5_IRQn=true\:0\:0\:false\:false\:true\:true\:true\:true
NVIC.ForceEnableDMAVector=true
NVIC.HardFault_IRQn=true\:0\:0\:false\:false\:true\:false\:false\:true
NVIC.MemoryManagement_IRQn=true\:0\:0\:false\:false\:true\:false\:false\:true
NVIC.NonMaskableInt_IRQn=true\:0\:0\:false\:false\:true\:false\:false\:true
NVIC.PendSV_IRQn=true\:0\:0\:false\:false\:true\:false\:false\:true
NVIC.PriorityGroup=NVIC_PRIORITYGROUP_4
NVIC.SDIO_IRQn=true\:0\:0\:false\:false\:true\:true\:true\:true
NVIC.SPI2_IRQn=true\:0\:0\:false\:false\:true\:true\:true\:true
NVIC.SPI4_IRQn=true\:0\:0\:false\:false\:true\:true\:true\:true
NVIC.SPI5_IRQn=true\:0\:0\:false\:false\:true\:true\:true\:true
NVIC.SVCall_IRQn=true\:0\:0\:false\:false\:true\:false\:false\:true
NVIC.SysTick_IRQn=true\:0\:0\:true\:false\:true\:false\:true\:true
NVIC.TIM1_UP_TIM10_IRQn=true\:15\:0\:false\:false\:true\:false\:true\:true
NVIC.TIM6_DAC_IRQn=true\:0\:0\:false\:false\:true\:true\:true\:true
NVIC.TIM7_IRQn=true\:0\:0\:false\:false\:true\:true\:true\:true
NVIC.TimeBase=TIM1_UP_TIM10_IRQn
NVIC.TimeBaseIP=TIM1
NVIC.UART7_IRQn=true\:0\:0\:false\:false\:true\:true\:true\:true
NVIC.UsageFault_IRQn=true\:0\:0\:false\:false\:true\:false\:false\:true
PA0.GPIOParameters=GPIO_Label
PA0.GPIO_Label=BAT_CG_WAKE_OUT
PA0.Mode=SYS_WakeUp0
PA0.Signal=SYS_WKUP1
PA1.GPIOParameters=GPIO_Label
PA1.GPIO_Label=ECG_MOSI
PA1.Locked=true
PA1.Mode=Full_Duplex_Master
PA1.Signal=SPI4_MOSI
PA10.GPIOParameters=GPIO_Label
PA10.GPIO_Label=PPG_MOSI
PA10.Locked=true
PA10.Mode=Full_Duplex_Master
PA10.Signal=SPI2_MOSI
PA11.GPIOParameters=GPIO_Label
PA11.GPIO_Label=ECG_MISO
PA11.Locked=true
PA11.Mode=Full_Duplex_Master
PA11.Signal=SPI4_MISO
PA12.GPIOParameters=GPIO_Label
PA12.GPIO_Label=VPP_EN
PA12.Locked=true
PA12.Signal=GPIO_Output
PA13.Locked=true
PA13.Mode=Serial_Wire
PA13.Signal=SYS_JTMS-SWDIO
PA14.Locked=true
PA14.Mode=Serial_Wire
PA14.Signal=SYS_JTCK-SWCLK
PA15.GPIOParameters=GPIO_PuPd,GPIO_Label
PA15.GPIO_Label=BLE_TX
PA15.GPIO_PuPd=GPIO_NOPULL
PA15.Locked=true
PA15.Mode=Asynchronous
PA15.Signal=UART7_TX
PA2.GPIOParameters=GPIO_Label
PA2.GPIO_Label=LCD_PWM
PA2.Locked=true
PA2.Signal=S_TIM9_CH1
PA3.GPIOParameters=GPIO_Label
PA3.GPIO_Label=BLE_MOD
PA3.Locked=true
PA3.Signal=GPIO_Output
PA4.GPIOParameters=GPIO_Label
PA4.GPIO_Label=SW2
PA4.Locked=true
PA4.Signal=GPXTI4
PA5.GPIOParameters=GPIO_Label
PA5.GPIO_Label=SW1
PA5.Locked=true
PA5.Signal=GPXTI5
PA6.GPIOParameters=GPIO_Label
PA6.GPIO_Label=SD_CMD
PA6.Locked=true
PA6.Mode=SD_4_bits_Wide_bus
PA6.Signal=SDIO_CMD
PA7.GPIOParameters=GPIO_Label
PA7.GPIO_Label=SW3
PA7.Locked=true
PA7.Signal=GPXTI7
PA8.GPIOParameters=GPIO_Label
PA8.GPIO_Label=SD_D1
PA8.Locked=true
PA8.Mode=SD_4_bits_Wide_bus
PA8.Signal=SDIO_D1
PA9.GPIOParameters=GPIO_Label
PA9.GPIO_Label=SD_D2
PA9.Locked=true
PA9.Mode=SD_4_bits_Wide_bus
PA9.Signal=SDIO_D2
PB0.GPIOParameters=GPIO_PuPd,GPIO_Label
PB0.GPIO_Label=LCD_SCK
PB0.GPIO_PuPd=GPIO_PULLUP
PB0.Locked=true
PB0.Mode=Simplex_Bidirectional_Master
PB0.Signal=SPI5_SCK
PB1.GPIOParameters=GPIO_Label
PB1.GPIO_Label=SP_PWM
PB1.Signal=S_TIM3_CH4
PB10.GPIOParameters=GPIO_Label
PB10.GPIO_Label=PPG_SCK
PB10.Locked=true
PB10.Mode=Full_Duplex_Master
PB10.Signal=SPI2_SCK
PB12.GPIOParameters=GPIO_PuPd,GPIO_Label
PB12.GPIO_Label=SD_SW
PB12.GPIO_PuPd=GPIO_PULLUP
PB12.Locked=true
PB12.Signal=GPIO_Input
PB13.GPIOParameters=GPIO_Label
PB13.GPIO_Label=ECG_SCK
PB13.Locked=true
PB13.Mode=Full_Duplex_Master
PB13.Signal=SPI4_SCK
PB14.GPIOParameters=GPIO_Label
PB14.GPIO_Label=PPG_MISO
PB14.Locked=true
PB14.Mode=Full_Duplex_Master
PB14.Signal=SPI2_MISO
PB15.GPIOParameters=GPIO_Label
PB15.GPIO_Label=SD_CLK
PB15.Locked=true
PB15.Mode=SD_4_bits_Wide_bus
PB15.Signal=SDIO_CK
PB2.GPIOParameters=GPIO_Label
PB2.GPIO_Label=LCD_DC
PB2.Locked=true
PB2.Signal=GPIO_Output
PB3.GPIOParameters=GPIO_PuPd,GPIO_Label
PB3.GPIO_Label=BLE_RX
PB3.GPIO_PuPd=GPIO_NOPULL
PB3.Locked=true
PB3.Mode=Asynchronous
PB3.Signal=UART7_RX
PB4.GPIOParameters=GPIO_Label
PB4.GPIO_Label=SD_D0
PB4.Locked=true
PB4.Mode=SD_4_bits_Wide_bus
PB4.Signal=SDIO_D0
PB5.GPIOParameters=GPIO_Label
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

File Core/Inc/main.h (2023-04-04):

/* USER CODE BEGIN Header */
/**
  ******************************************************************************
  * @file           : main.h
  * @brief          : Header for main.c file.
  *                   This file contains the common defines of the application.
  ******************************************************************************
  * @attention
  *
  * Copyright (c) 2022 STMicroelectronics.
  * All rights reserved.
  *
  * This software is licensed under terms that can be found in the LICENSE file
  * in the root directory of this software component.
  * If no LICENSE file comes with this software, it is provided AS-IS.
  *
  ******************************************************************************
  */
/* USER CODE END Header */

/* Define to prevent recursive inclusion -------------------------------------*/
#ifndef __MAIN_H
#define __MAIN_H

#ifdef __cplusplus
extern "C" {
#endif

/* Includes ------------------------------------------------------------------*/
#include "stm32f4xx_hal.h"

/* Private includes ----------------------------------------------------------*/
/* USER CODE BEGIN Includes */

#include <stdio.h>
#include <string.h>
#include <stdlib.h>
#include <math.h>
#include <stdbool.h>

/* USER CODE END Includes */

/* Exported types ------------------------------------------------------------*/
/* USER CODE BEGIN ET */

/* USER CODE END ET */

/* Exported constants --------------------------------------------------------*/
/* USER CODE BEGIN EC */
typedef enum {
	LCD_MAINSCREEN = 0,
	LCD_MENUSCREEN = 1,
	LCD_PPGSCREEN = 2,
	LCD_ECGSCREEN = 3,
	LCD_AFSCREEN = 4,
	LCD_SAVESCREEN = 5,
	LCD_SERVERSCREEN = 6
} LCD_SCREEN_TYPE;
/* USER CODE END EC */

/* Exported macro ------------------------------------------------------------*/
/* USER CODE BEGIN EM */
typedef struct __attribute__((__packed__)) {
	uint32_t tag : 4;
	int32_t data : 20;
}MAX86171;

typedef struct __attribute__((__packed__)) {
	uint32_t	tag  : 3;	/* ETAG data from the ECG_FIFO	*/
	uint32_t	step : 11;	/* time step of the sample		*/
  int32_t		data : 18;	/* voltage of the sample		*/
}MAX30003;

/* USER CODE END EM */

void HAL_TIM_MspPostInit(TIM_HandleTypeDef *htim);

/* Exported functions prototypes ---------------------------------------------*/
void Error_Handler(void);

/* USER CODE BEGIN EFP */

/* USER CODE END EFP */
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

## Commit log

2022-11-17 AF detect
    [MCU.kicad_sch, MCU_Power.kicad_sch, MCU_peripheral.kicad_sch, Sensor.kicad_sch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]
2023-04-04 selective Afib detection prototype

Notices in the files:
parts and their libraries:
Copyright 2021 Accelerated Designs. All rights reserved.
